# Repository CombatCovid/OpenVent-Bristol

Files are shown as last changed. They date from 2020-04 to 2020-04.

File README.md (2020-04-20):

OpenVent 

## Readme taken from the original repo: https://github.com/RealFreshRate/OpenVent/tree/master
Introduction 

Ventilation is the only known available treatment for sufferers of COVID-19. Existing ventilation machines in hospitals are complex general purpose machines costing £10s of thousands. The availability of the existing ventilators is no where near enough to meet the predicted required numbers, for example in the UK around 5000 ventilators currently exist within the NHS but it is predicted they will need around 30,000 in just a few weeks. Critically ill patients left without ventilation treatment are in danger of losing their life.

As far as I understand, one effect of the virus as well as damaging the lungs, it also produces a very sticky mucus in the lungs which causes the lungs to collapse and makes it very difficult for the patent to breath of their own accord. Ventilation can be delivered either via intubation or a well sealed mask and delivers continuous positive air pressure into the lungs to keep them inflated at all times. Conscious less ill patents can be aided using a CPAP (Continuous Positive Airway Pressure) ventilation device like a sleep apnea device, this delivers a constant air of the same flow rate and pressure. The more critically ill patients need a machine to breath for them which varies the pressure and flow according to inhale and exhale and relies on maintaining a good seal and a PEEP valve to keep the lungs continually inflated.

An analogy: Imagine inflating a balloon, letting it deflate completely, then re-inflating it, that is like CPAP. If you inflated the balloon, deflated it half way, then re-inflated it, that's more like the treatment needed for the worse sufferers.

Assumptions

1. BVM design does not vary drastically, with the same basic diameters required to fit within the frame. 
2. That whomever produces this is able to produce the physical components to a standard. 
3. That on average a human breaths between 8-30 breathes per minute depending on a number of factors.  
4. Humans can start having negative effects from asphyxia in around 90 seconds. 
5. That the figure of tje global average of around 1 doctor to 10 intensive paitents.
6. Power at some point could be lost or be inconsistent from source. 

Design Principles

1. for a very simple low cost design.

2. made using readily available components.

3. that can be manufactured quickly and easily in small quantities or on mass at low cost.

4. to work reliably and with the lowest risk to the patient.

Restrictions

It is our intention to rework the code over time to improve the safety margins and reliability by reworking the code against a industry recognised standard. As part of this we are/will be applying based off NASA's The Power of Ten (http://spinroot.com/gerard/pdf/P10.pdf). We have listed them below, for reference when making changes to the code. 

1. Restrict all code to very simple control flow contructs. This means NO goto, setjmp, longjmp or recursion. 
2. All loops must have fixed upper bounds. It must be easy to test if the upper bounds have been exceeded. 
3. After initialisation, there should be no dynamic memory allocation. 
4. No greater than 60 lines of code per function. Controls the amount of memory. 
5. On average no less than 2 assertions per function. Each function should have some form of check in 
6. Data objects must be declared at the smallest scope. Avoid declaring filtered or changed data objects. 
7. Check the validity of the parameters used inside the function it's being used in.
8. The use of preprocessor must be limited to the inclusion of header files and simple marcos. All macros will be expressed in complete syntax in the code. 
9. Restrict the use of pointers to one layer of referencing. 
10. Make sure you have you complier set to it's most stringent, make sure the code executes with ANY errors. 

Limitations

1. At this time these rules have only be partly applied to the current version of the code, do not assume that these have been enforced.

2. There is no test currently for checking if the motor has been wired correctly. So testing without a bag hooked up is nessesary.

3. Doesn't meet the NHS requirements at this time, but it is the intention to get as close as practicable. 

**Improvement for next version**
  - Pressure sensor + buzzer
  - Test pressure sensor with test lung
  - Impliment safety alarm (auidable & visual) code with pressure sensor (including timeouts)
  - Secure the bag down better
  - Remove global variables
  - Add LCD screen + button shield to read back pressure valves & other valves
  - Add auto switch-over to battery back up
  - Add voltage divider & safety code to give auidable & visual alarm when battery is running out
  - Code in the motorSpeed POT to allow adjustment for different motors

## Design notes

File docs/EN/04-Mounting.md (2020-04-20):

# Step 3 : Mount the motor

As shown in the pictures;

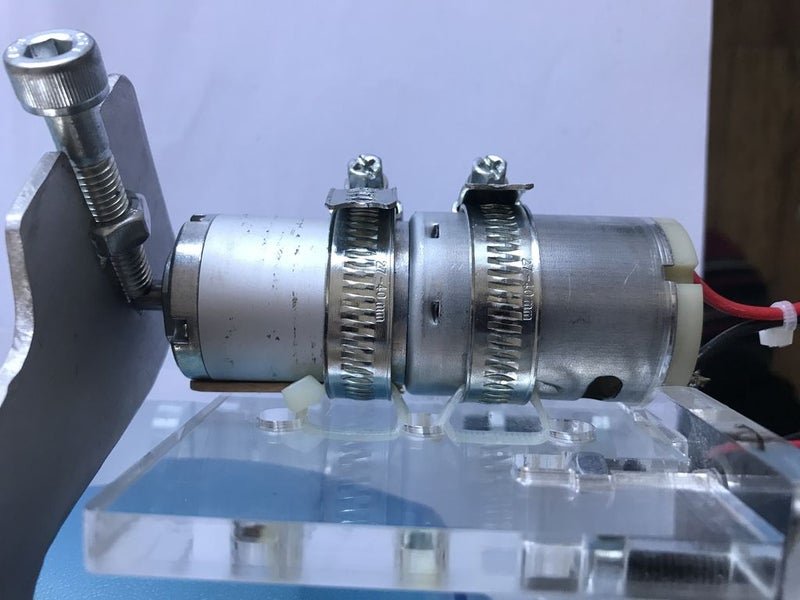
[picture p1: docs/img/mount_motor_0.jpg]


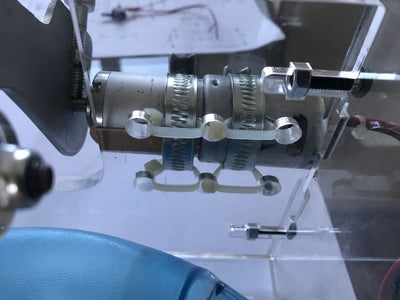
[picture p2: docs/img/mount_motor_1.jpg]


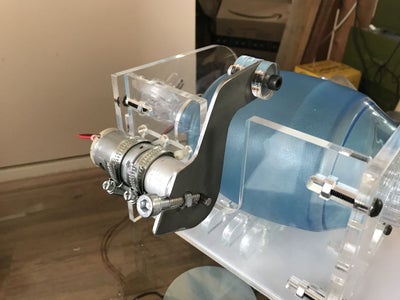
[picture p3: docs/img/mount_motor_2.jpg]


- attach 4 cable ties (the beefier the better) through the 6 holes in the back plate such that 4 of them sit parallel to each other in the horizontal axis
- then pass 2 jubilee clips (I used 25-40mm clips) through the loops in the cable ties and around the motor.
- Then tighten the clips until it grips the motor nicely, but don't tighten it too much!!! Because it can crush the casing and damage the motor.

# Step 4: Mount motor arm

Attach the motor arm using the M8 nut and bolt. Hold the nut in its 'captive' slot and tighten the bolt up against the flat of the motor shaft with a hex key.

Attach some of the small laser cut circles to the end of the arm with the long M6 bolt and nut to distribute the pressing force on the bag. It is best to use a niloc M6 nut if you have one here. You may also want to add some bubble wrap or fabric around the end of the arm for extra cushioning as it may wear into the bag over extended use.

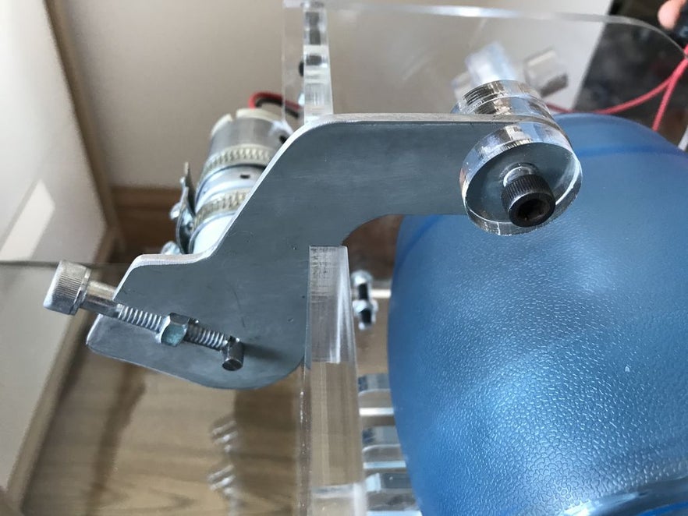
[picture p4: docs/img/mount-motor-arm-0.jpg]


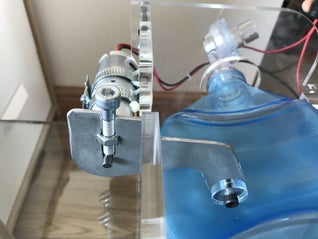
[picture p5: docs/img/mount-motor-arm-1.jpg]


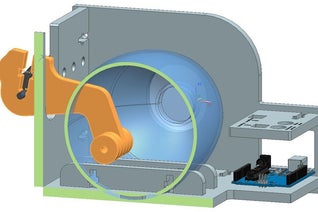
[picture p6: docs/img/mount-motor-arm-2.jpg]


# Step 5: Electronics

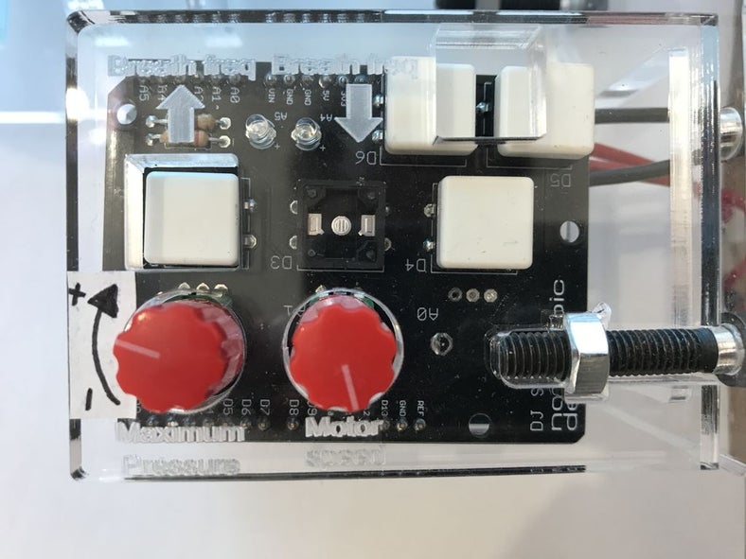
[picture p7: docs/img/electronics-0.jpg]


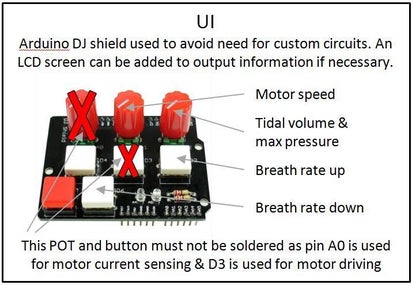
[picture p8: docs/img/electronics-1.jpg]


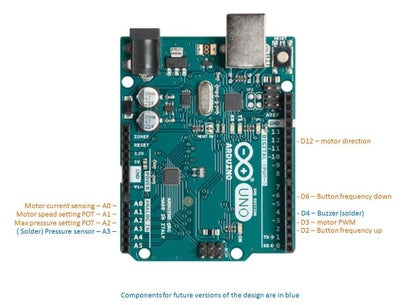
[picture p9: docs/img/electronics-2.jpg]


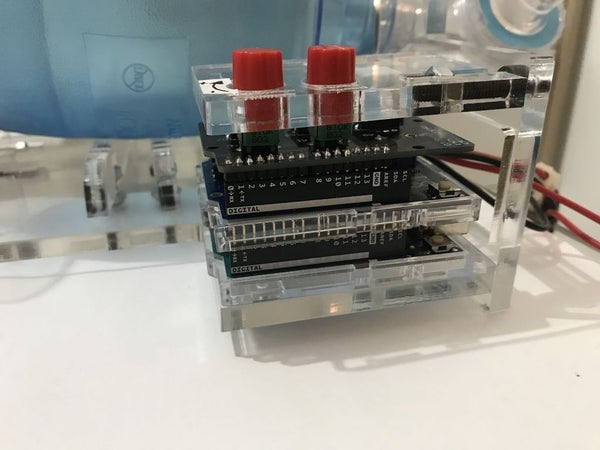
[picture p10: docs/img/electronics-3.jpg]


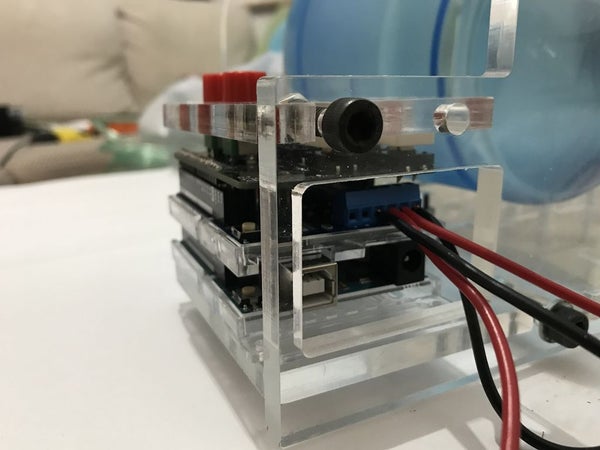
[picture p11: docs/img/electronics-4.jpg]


- Connect up the motor to motor port A of the motor driver shield
- Connect up the 12V power supply to the Vin connections of the motor driver shield (don't be tempted to plug your power supply direct into the Arduino board, it doesn't seem to like this)
- Connect up your switch in line with the power supply and mount your switch into the 6.35mm hole in the side panel
- Solder up your DJ shield but take care to only solder the components listed below as pins A0 and D3 are needed by the motor driver
- The POT on A1
- The POT on A2
- The button on D6
- The button on D2
- Stack the motor driver shield and the DJ shield on top of the Arduino and secure them in place with the laser cut UI panel using an M6 nut and bolt

# Step 6: Software

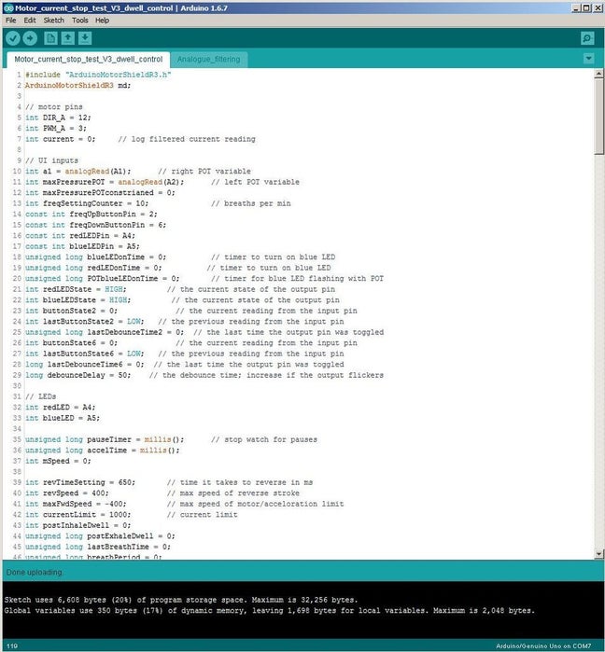
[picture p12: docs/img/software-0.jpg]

Download the latest version of my Arduino code from GitHub using the following link: https://github.com/RealFreshRate/OpenVent/tree/master/Motor_current_stop_test

- Upload the code to the board but before you run it for the first time **make sure the "max pressure/tidal volume" POT is dialed all the way down (all the way anti clockwise).**

- **Once you run it for the first time be prepared to stop it quickly because you have a 50/50 chance that the motor is spinning in the right direction.**
- If the motor trys to spin the wrong way initially then swap the motor wires around to reverse the polarity, if that doesn't work then gradually increase the current limit by dialing up the "max pressure" POT because bigger motors could be tripping out of the current limit upon startup.
-  I think the current limit range on the POT is from 800mA to 1.2A.

# Step 7 :  Enjoy!

Don't forget to add you PEEP valve and mask extension tube, then test and enjoy!

There is a running list of improvements we are keeping for the next version on the GitHub readme: https://github.com/RealFreshRate/OpenVent

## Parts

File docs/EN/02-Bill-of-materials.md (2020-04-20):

# BOM 

# Step 1:Buy the parts
- Arduino Uno £3.00, [buy here](https://www.ebay.co.uk/itm/Mega2560-UNO-R3-ATmega328P-ATemga2560-16AU-Board-CH340G-FT232-Chip-Arduino-UK/202460399703?hash=item2f23948857:m:msxh1rbsMICGKlrlhEPiOeA) (a genuine Uno board was used in the prototype)

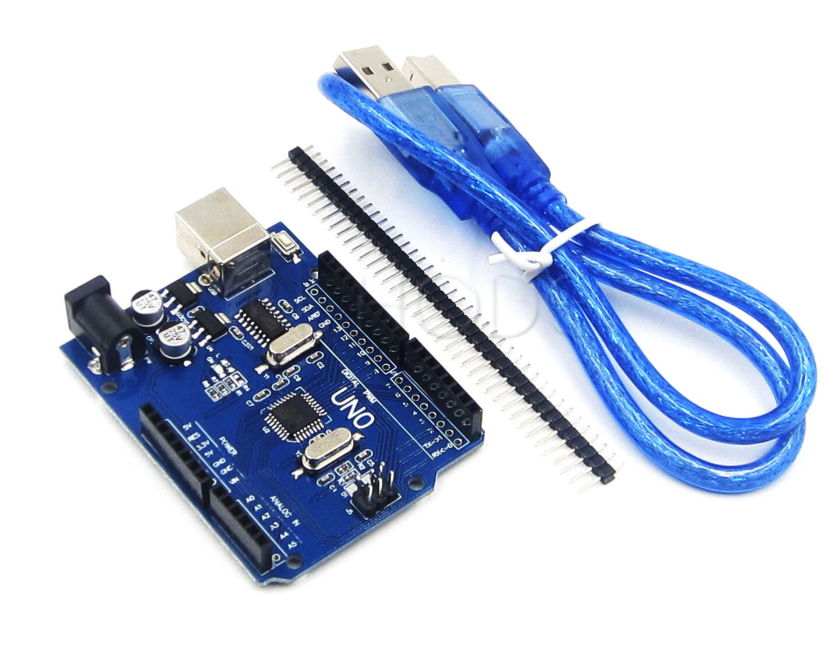
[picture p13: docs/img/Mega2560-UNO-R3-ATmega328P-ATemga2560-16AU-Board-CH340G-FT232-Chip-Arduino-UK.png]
Mega2560-UNO-R3-ATmega328P-ATemga2560-16AU-Board-CH340G-FT232-Chip-Arduino-UK


- Arduino motor driver shield rev 3 £10,[buy here](https://www.ebay.co.uk/itm/L298P-Shield-R3-DC-Motor-Driver-Module-2A-H-Bridge-2-way-Arduino-UNO-2560-L40/142913731149?hash=item2146527a4d:g:Ju0AAOSwuNFbfdvW)

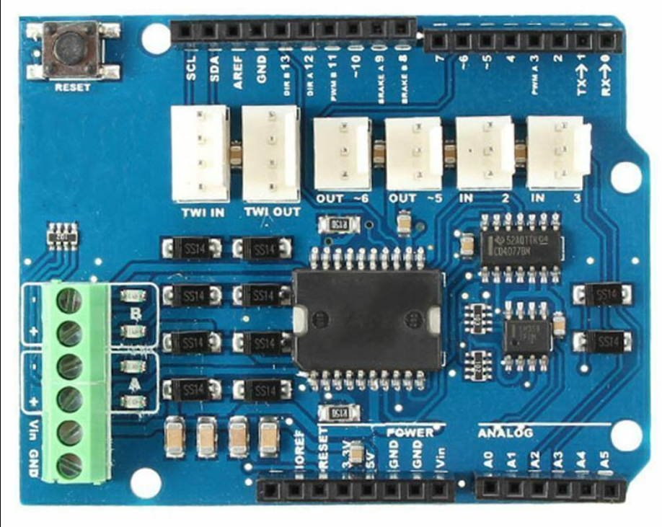
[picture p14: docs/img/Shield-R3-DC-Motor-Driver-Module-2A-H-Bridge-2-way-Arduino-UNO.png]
Shield-R3-DC-Motor-Driver-Module-2A-H-Bridge-2-way-Arduino-UNO


- Geared DC motor 20-40rpm £24.00,[buy here](https://uk.rs-online.com/web/p/dc-geared-motors/0420586/)

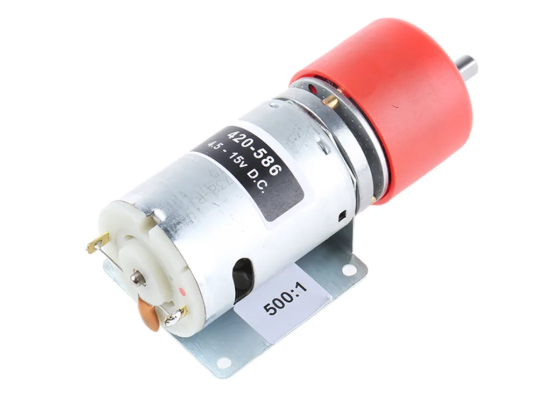
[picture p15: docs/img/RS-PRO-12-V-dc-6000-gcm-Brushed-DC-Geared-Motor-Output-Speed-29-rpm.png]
RS-PRO-12-V-dc-6000-gcm-Brushed-DC-Geared-Motor-Output-Speed-29-rpm


- Arduino Dj shield £16.00 [Buy Here](https://coolcomponents.co.uk/products/dj-shield-standard-kit?_pos=2&_sid=3e205c697&_ss=r)

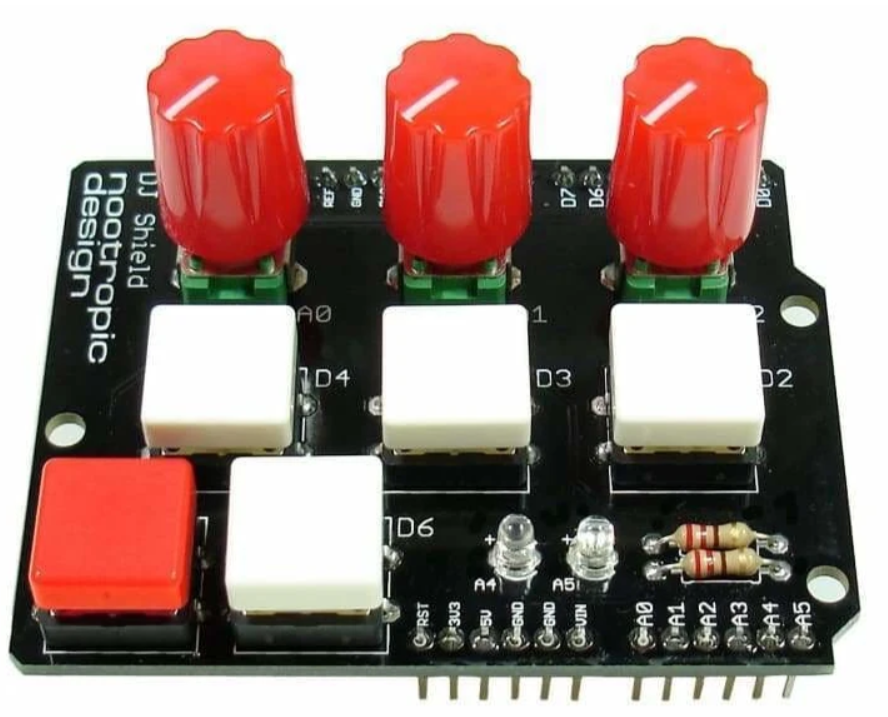
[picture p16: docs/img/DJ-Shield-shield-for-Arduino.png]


- Mains to 12 V DC 'wall wart' min 3A £5 [Buy Here](https://www.ebay.co.uk/itm/EU-UK-Universal-DC-12V-1A-2A-3A-Mains-Power-Supply-Adapter-Charger-Transformer/264587958141?hash=item3d9aabd77d:m:miZdzji8t2vXFunw-isefxA)

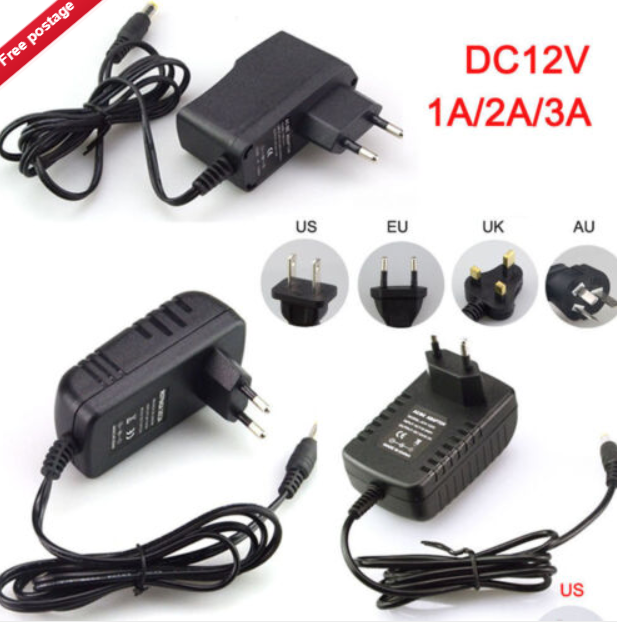
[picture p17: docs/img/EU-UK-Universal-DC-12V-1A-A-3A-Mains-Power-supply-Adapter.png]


- On/off switch £1.00 any switch will do, I used a push button latching 16mm panel mount switch, the one in the link is another example [](https://uk.rs-online.com/web/p/toggle-switches/7347062/)

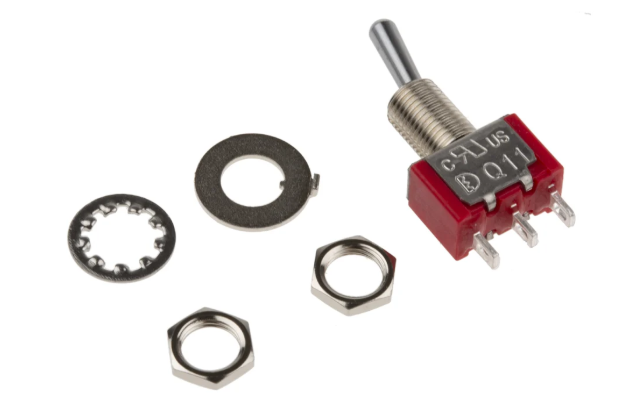
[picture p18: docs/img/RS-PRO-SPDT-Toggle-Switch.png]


- 4x cable ties/zip ties (beefier the better)
- 2x jubilee clips 25-40mm
- 9x M6x25mm bolts
- 4x M6x15mm bolts
- 13x M6 nuts
- 1x niloc M6 nut
- 1x M8 x 40mm bolt
- 1x M8 nut
- Laser cut 8mm acrylic parts for chassis £10-£30 (depending on how friendly your local laser cutting place is)
- Laser cut 3mm aluminium motor arm £5-20£ (depending on how friendly your local laser cutting place is)Totaling around £80 (excluding the medical parts; BVM etc.)

- DXFs for laser cutting are stored on GrabCAD in this link: [https://grabcad.com/library/covid-19-rapid-manufacture-ventilator-bvm-ambubag-openvent-bristol-2](https://grabcad.com/library/covid-19-rapid-manufacture-ventilator-bvm-ambubag-openvent-bristol-2)
- Other things not listed here that you will need for treating COVID-19 are a PEEP valve with valve ring adapter, a mask extension tube and a soft Velcro mask strap.

**- A list of improvements for the next version is kept in the GitHub readme, some of those things are below:**

- A 12V battery backup with at least 20 min run time
- A battery management circuit to automatically switch over to the battery in a power cut
- A pressure sensor alarm for sensing failure and a buzzer & LED to create an alert
- An LCD screen to show pressure and other values and settings

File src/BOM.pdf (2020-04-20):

# Instructables

# Step # 1:Buy the parts

Arduino Uno £3.00, buy here (https://www.ebay.co.uk/itm/Mega2560-UNO-R3-ATmega328P-ATemga2560-16AU-Board-CH340G-FT232-Chip-Arduino-UK/202460399703) (a genuine Uno board was used in the prototype)

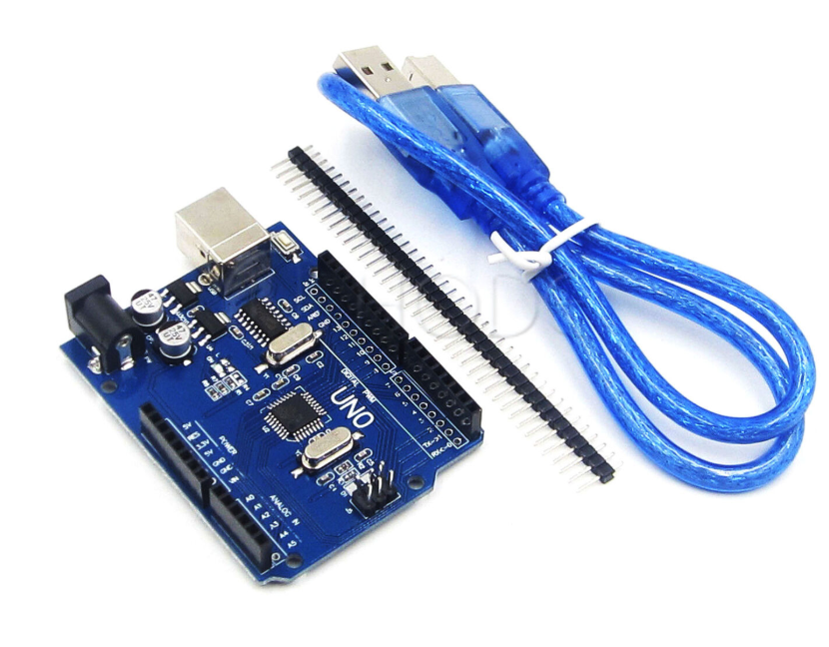
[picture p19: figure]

Arduino motor driver shield rev 3 £10,buy here (https://www.ebay.co.uk/itm/L298P-Shield-R3-DC-Motor-Driver-Module-2A-H-Bridge-2-way-Arduino-UNO-2560-L40/142913731149)

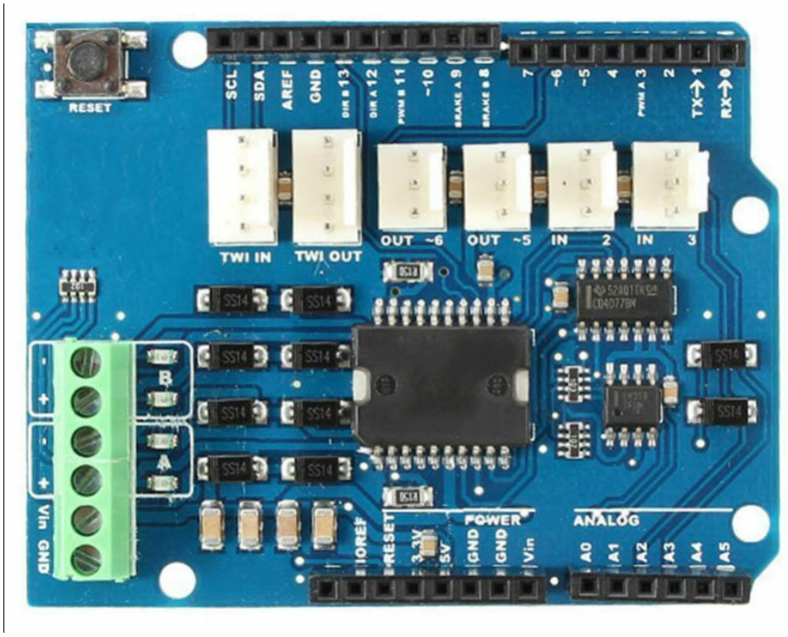
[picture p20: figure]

Geared DC motor 20-40rpm £24.00,buy here (https://uk.rs-online.com/web/p/dc-geared-motors/0420586/)


Arduino Dj shield £16.00 Buy Here (https://coolcomponents.co.uk/products/dj-shield-standard-kit?_pos=2&_sid=3e205c697&_ss=r)


Mains to 12 V DC ‘wall wart’ min 3A £5 Buy Here (https://www.ebay.co.uk/itm/EU-UK-Universal-DC-12V-1A-2A-3A-Mains-Power-Supply-Adapter-Charger-Transformer/264587958141)


On/off switch £1.00 any switch will do, I used a push button latching 16mm panel mount switch, the one in the link is another example


4x cable ties/zip ties (beefier the better) 2x jubilee clips 25-40mm
9x M6x25mm bolts
4x M6x15mm bolts
13x M6 nuts
1x niloc M6 nut
1x M8 x 40mm bolt
1x M8 nut
Laser cut 8mm acrylic parts for chassis £10-£30 (depending on how friendly your local laser cutting place is)
Laser cut 3mm aluminium motor arm £5-20£ (depending on how friendly your local laser cutting place is)Totaling around £80 (excluding the medical parts; BVM etc.)
DXFs for laser cutting are stored on GrabCAD in this link: https://grabcad.com/library/covid-19-rapid-manufacture-ventilator-bvm-ambubag-openvent-bristol-2 (https://grabcad.com/library/covid-19-rapid-manufacture-ventilator-bvm-ambubag-openvent-bristol-2)
Other things not listed here that you will need for treating COVID-19 are a PEEP valve with valve ring adapter, a mask extension tube and a soft Velcro mask strap.
- A list of improvements for the next version is kept in the GitHub readme, some of those things are below:

A 12V battery backup with at least 20 min run time
A battery management circuit to automatically switch over to the battery in a power cut

A pressure sensor alarm for sensing failure and a buzzer & LED to create an alert An LCD screen to show pressure and other values and settings

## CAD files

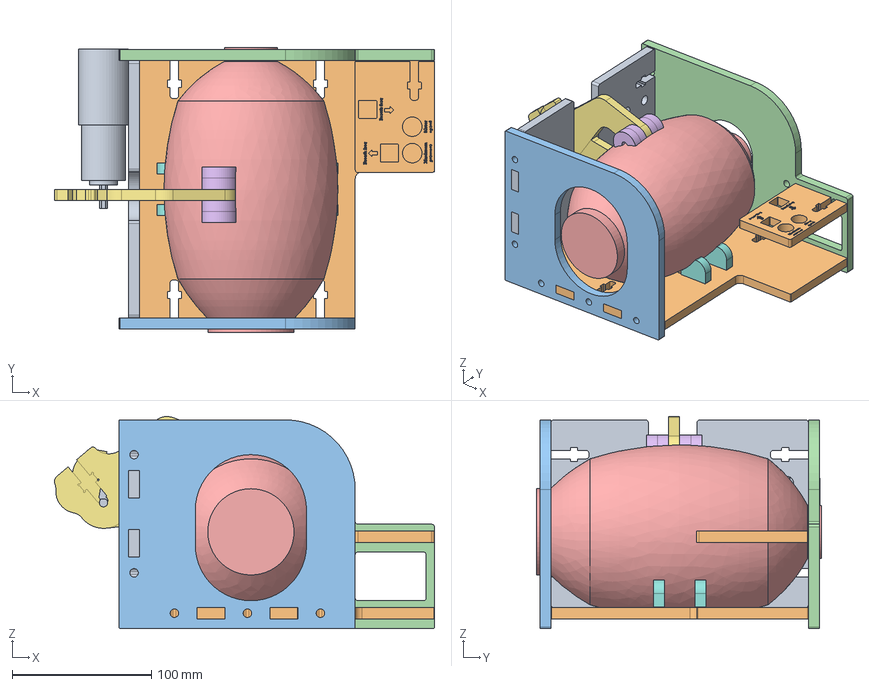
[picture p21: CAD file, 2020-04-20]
src/Ventilator assy V1.1.stp
273.2 x 205.0 x 152.4 mm
Back plate
Base plate
Left side big hole
right side small hole
ambu bag V1
arm contact ring x 8
Base fins x 2
DC geared motor 454 0899
Arduino DJ shield cover V2

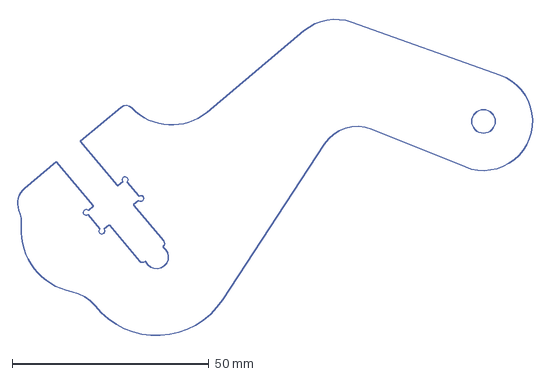
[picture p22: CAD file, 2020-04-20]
src/Motor arm V2.dxf
132.0 x 81.5 mm

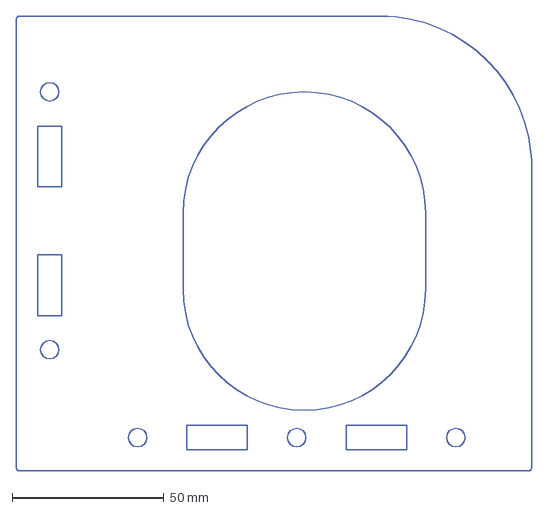
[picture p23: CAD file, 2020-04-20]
src/Left side big hole.dxf
170.0 x 150.0 mm

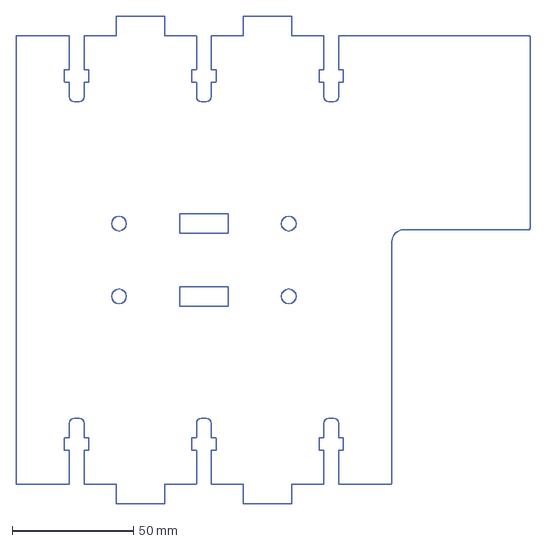
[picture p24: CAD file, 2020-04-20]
src/Base plate.dxf
212.0 x 201.0 mm

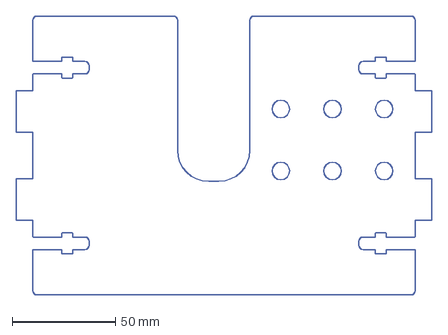
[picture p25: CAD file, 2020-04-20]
src/Back plate.dxf
201.0 x 135.0 mm

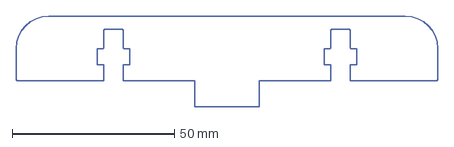
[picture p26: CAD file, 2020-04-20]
src/Base fins.dxf
130.0 x 28.0 mm

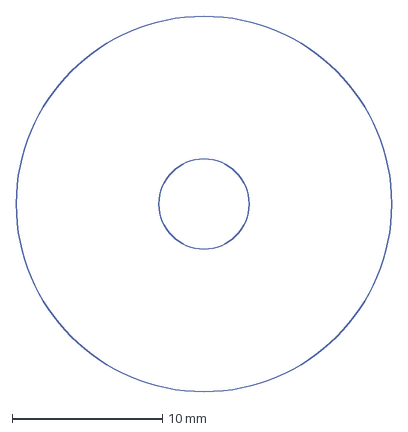
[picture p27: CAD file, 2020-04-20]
src/arm contact ring 25mm.dxf
25.0 x 25.0 mm

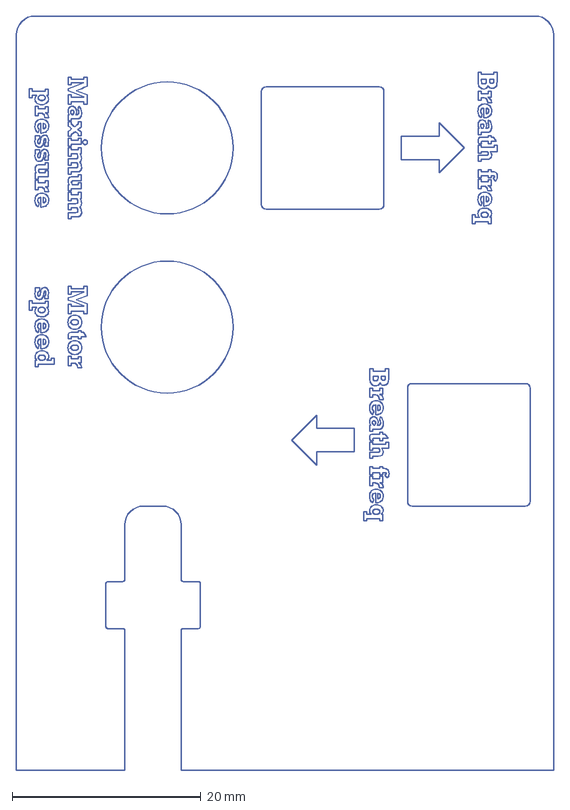
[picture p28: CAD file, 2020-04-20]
src/Arduino DJ shield cover V2.dxf
57.0 x 80.0 mm

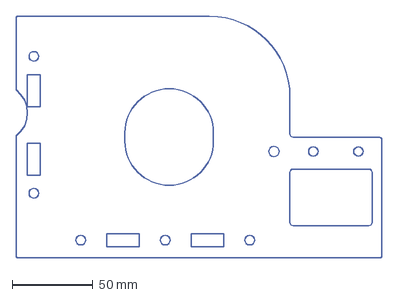
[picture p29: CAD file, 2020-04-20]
src/right side small hole.dxf
227.0 x 150.0 mm

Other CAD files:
src/Ventilator assy V1.stp

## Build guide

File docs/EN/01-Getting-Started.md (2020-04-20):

# Getting started
The project link is : [https://www.instructables.com/id/COVID-19-Rapid-Manufacture-Ventilator-BVM-Ambubag-/](https://www.instructables.com/id/COVID-19-Rapid-Manufacture-Ventilator-BVM-Ambubag-/)
The repo  with this documentation can be downloaded following this link: [DOWNLOAD HERE](https://github.com/CombatCovid/OpenVent-Bristol/archive/master.zip)

The USP(Unique Selling Proposition) of this design is how easy and fast it can scale for mass production for the following reasons:

- Automated production: The production of each part is fully automated (laser cutting), with only 8 different parts
- Only 6 off-the-shelf components: Very few different components are needed and no exotic parts are needed (not even a motor coupling)
- Simple mechanism: It uses a super simple mechanism with just an arm mounted to a motor - no complicated mechanisms to go wrong, just one moving part
- Fast assembly: Complete assembly is possible in around 20 min with one person
- Adjustable settings: Has full adjustment of breath frequency and pressure/tidal volume and with a small adaption can function within all NHS requirements
- Low cost

See it here: [https://youtu.be/jutBw_xIwTw](https://youtu.be/jutBw_xIwTw)

# Disclaimer 

I'm not selling this product, just releasing the design as open source to help others. 

**This design doesn't currently meet the NHS requirements (in link below) and does not have medical product approval which will be needed for treatment**. 
A list of improvements for the next version with the aim of meeting the NHS spec is kept in the GitHub readme (link below), some of those things are here:

- A 12V battery backup with at least 20 min run time
- A battery management circuit to automatically switch over to the battery in a power cut (not actually required but would seem sensible)
- A pressure sensor alarm for sensing failure and a buzzer & LED to create an alarm on failure
- An LCD screen to show pressure and other values and Settings
GitHub code link: [https://github.com/RealFreshRate/OpenVent](https://github.com/RealFreshRate/OpenVent)

NHS Rapidly manufactured ventilator system specification: [https://www.gov.uk/government/publications/specification-for-ventilators-to-be-used-in-uk-hospitals-during-the-coronavirus-covid-19-outbreak](https://www.gov.uk/government/publications/specification-for-ventilators-to-be-used-in-uk-hospitals-during-the-coronavirus-covid-19-outbreak)

- All users of this design and device shall be deemed notified of the warnings stated herein. 
- This device is a simply designed, fast produced ventilator. This device should not be used in place of an existing hospital ventilator. 
- These should only be used as a last resort where a patient has no other alternative due to the lack of availability of existing ventilators. 
- **This is not a fully medically certified device and should not be relied upon as such. The device is designed for use by trained medical professionals and should only be used by trained medical professionals; it is not intended for home use.**
- The designers and manufacturers of this device shall not be held liable for any death or injury that may result from this device.
- The designers and manufacturers of this device give no guarantees or warranties as to the efficacy and/or safety of this device.
- This design isn't connected with dyson or any other ventilator projects including Dyson CoVent.

# Problem statement

Ventilation is the only known available treatment for sufferers of COVID-19. 
Existing ventilation machines in hospitals are complex general purpose machines costing £10s of thousands. The availability of the existing ventilators is no where near enough to meet the predicted required numbers, for example in the UK around 5000 ventilators currently exist within the NHS but it is predicted they will need around 30,000 in just a few weeks. Critically ill patients left without ventilation treatment are in danger of losing their life.

As far as I understand, one effect of the virus as well as damaging the lungs, it also produces a very sticky mucus in the lungs which causes the lungs to collapse and makes it very difficult for the patent to breath of their own accord. Ventilation can be delivered either via intubation or a well sealed mask and delivers continuous positive air pressure into the lungs to keep them inflated at all times. Conscious less ill patents can be aided using a CPAP (Continuous Positive Airway Pressure) ventilation device like a sleep apnea device, this delivers a constant air of the same flow rate and pressure. The more critically ill patients need a machine to breath for them which varies the pressure and flow according to inhale and exhale and relies on maintaining a good seal and a PEEP valve to keep the lungs continually inflated.

An analogy: Imagine inflating a balloon, letting it deflate completely, then re-inflating it, that is like CPAP. If you inflated the balloon, deflated it half way, then re-inflated it, that's more like the treatment needed for the worse sufferers.

**The aim is:**

1. for a very simple low cost design

2. made using readily available components

3. that can be manufactured quickly and easily in small quantities or on mass at low cost

4. to work reliably and with the lowest risk to the patient (partly to help speed up the medical product approval process, if this project gets that far)

# Design

This design is based on a hand operated BVM (Bag Valve Mask) or known as ambu bag, which when combined with a PEEP valve will meet most of the NHS requirements for COVID-19 ventilation treatment. My design replaces the hand making this automated.

### Side and Top views

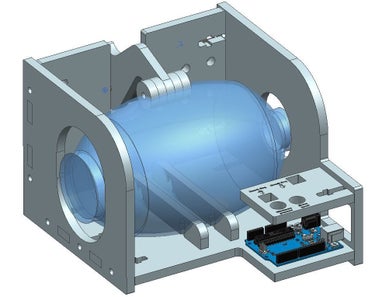
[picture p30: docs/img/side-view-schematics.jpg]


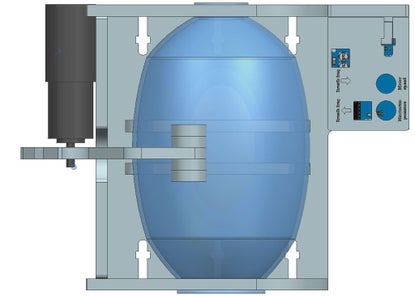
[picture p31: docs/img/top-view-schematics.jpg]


## Credits:

Credit to the people below for helping to make this all possible:

**Sam Reilly - Software Certification Engineer
Sadie - ITU nurse
Tom Breddal
Consultant Anesthetist in UK ITU**

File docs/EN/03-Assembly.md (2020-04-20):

# Step 2: Laser Cut and Assemble Chassis

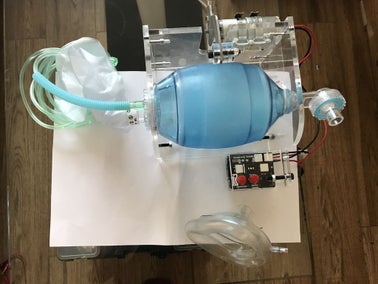
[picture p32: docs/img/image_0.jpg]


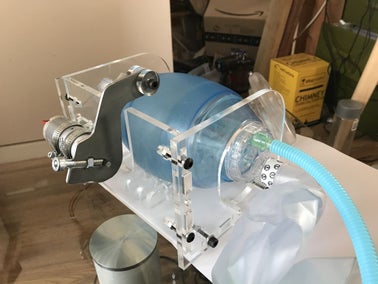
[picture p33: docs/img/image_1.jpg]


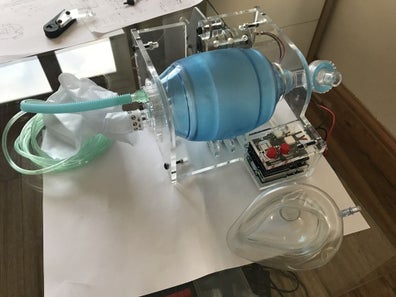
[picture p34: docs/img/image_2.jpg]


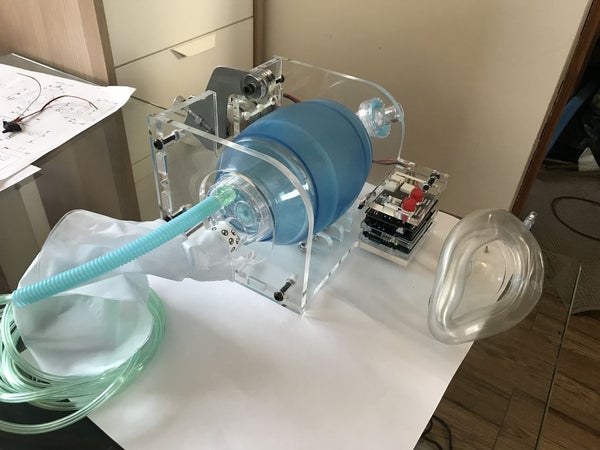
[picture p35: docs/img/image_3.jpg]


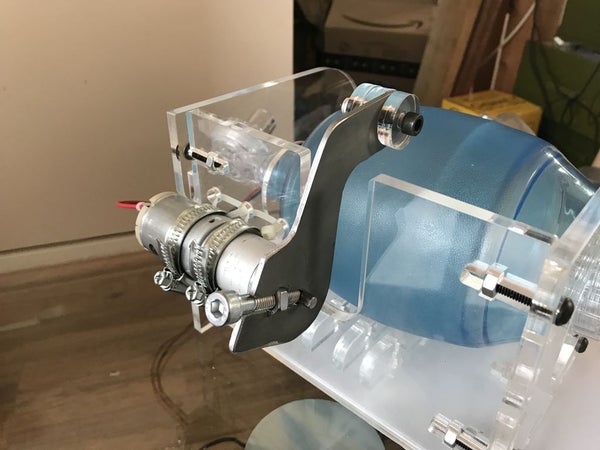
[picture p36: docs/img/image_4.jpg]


DXF files and STEP file of the assembly are stored on GrabCAD in this link: [https://grabcad.com/library/covid-19-rapid-manufacture-ventilator-bvm-ambubag-openvent-bristol-2](https://grabcad.com/library/covid-19-rapid-manufacture-ventilator-bvm-ambubag-openvent-bristol-2)

Laser cut the following part files from 8mm acrylic or ply with the following quantities:

- Q1x "Back plate.dxf"
- Q1x "Left side big hole.dxf"
- Q1x "Base plate.dxf"
- Q1x "Arduino DJ shield cover V2.dxf"
- Q1x "right side small hole.dxf"
- Q4x "arm contact ring 25mm.dxf"
- Q2x "Base fins"

**All these parts are in the ```SRC FOLDER``` in the root of the repo**
To assemble you will need:

1. 9x M6x25mm bolts
2. 4x M6x15mm bolts
3. 14x M6 nuts

Watch this video for time-lapse assembly and refer to photos for what it should look like. Apologies for the poor quality and note I was using a older design of motor mount in this video which has been updated, see next step for up to date motor mount method.

### A video about how to assembly the parts

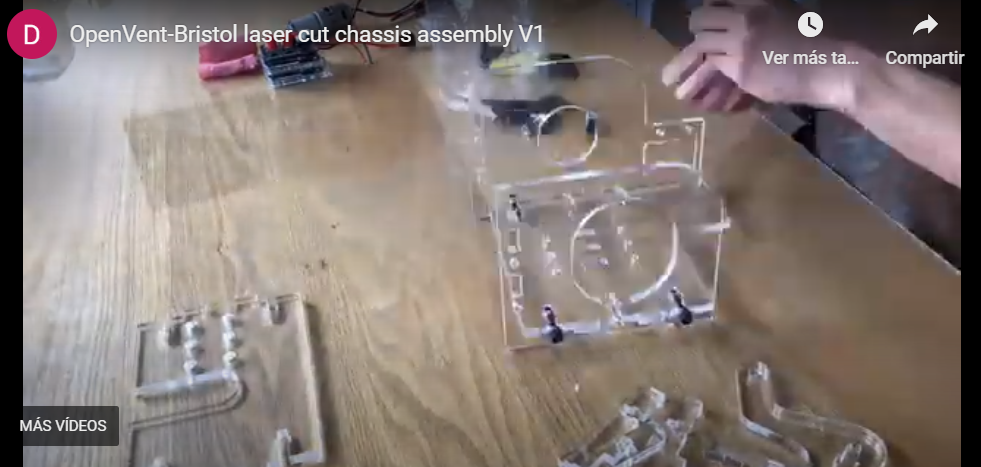
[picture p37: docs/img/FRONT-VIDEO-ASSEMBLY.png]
WATCH VIDEO HERE (https://youtu.be/DLQxyWLqXpQ)
